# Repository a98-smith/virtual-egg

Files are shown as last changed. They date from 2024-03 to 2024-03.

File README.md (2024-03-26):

# Simulated Fragile Object (Virtual Egg)

## Project Description:

The Virtual Eggs Test (Clemente et al.,2015) was adapted from the Box and Blocks Test in order to evaluate the dexterity of sensory enabled prostheses. For their initial studies, origami boxes and spaghetti strands were used as their simulated fragile object (egg). This method of construction while informative, simple and cost effective has limitations for use outside of laboratory settings. For example, it would be potentially challenging for an individual with upper limb loss to construct or reset the aparatus without the presence of another individual which could impact engagement in 'in-the-wild' test scenarios.

In order to address this, this repo contains the [.stl](Assembly%20stls) and [technical drawings](Technical%20Drawings) for a passive and reusable egg design. The design can be altered to provide various levels of fragility, and can easily be reset and re-used with a single hand while requiring little to no manual dexterity.

The following section details the construction of the egg.

## Manufacturing and Assembly Instructions:

The egg consists of [6 main components](Technical%20Drawings/Assembly%20Drawings.pdf):
- **Shell:** The outer casing for the egg
- **Slide:** The sliding plates used to grasp the object
- **Midplate:** This is used as a back-board for the spring-loaded plates and combine with the Runner top ensure square travel.
- **GravLock:** Small pins used to lock the egg when too much force is applied (the egg is crushed) through gravity.
- **Runner:** Ensures square travel of the Slide throughout the range of motion.
- **Spring:** Provides a method of calibrating the fragility of the object, along with returning the Slide to it's original position.

### 1. Manufacture
The main structural components for the egg are 3D printed in PLA. The parts are designed with a low tolerance to ensure smooth travel, however some simple post-processing may be necessary for correct operation.

For each egg the printed parts list is:
- 2 x [**Shell**](Assembly%20stls/Shell.stl)
- 2 x [**Slide**](Assembly%20stls/Slide.stl)
- 1 x [**Midplate**](Assembly%20stls/Midplate.stl)

The remainder of the manufactured parts, are made from brass dowelling with a rounded end:
- 2 x **Runner** (⌀5.2mm)
- 4 x **GravLock** (⌀2mm)

The **Spring** should be a compression based spring, with an id > ⌀6mm, and an un-compressed length of ~30mm. The _k_-value of the **Spring** will determine the relative fragility of the egg and should be chosen with your experimental set-up in mind. 

### 2. Assembly
    
1. Affix **Runner** to central extrusion of **Slide** using an epoxy adhesive.
2. Insert **GravLock** into each hole on the bottom of the **Slides**.
3. Insert **Slide** into **Shell** ensuring the **GravLocks** are facing the correct direction (rounded end down).
4. Lubricate the contact surfaces of the **Shell** and **Runner**.
    - Both _Super Lube Multipurpose Synthetic Grease_ and fibreglass tape have proven to be effective in isolation but combined for best results.
5. Slot your selected **Spring** over the **Runner**, and the other end over the extrusion on **Midplate**.
6. Align the edges and adhere the back surface of **Shell** against **Midplate** maintaining gentle pressure.
7. Repeat this process for the second side.

> I hope this may be of use to someone, and if there are any questions or if anything about the process is unclear send me a message.

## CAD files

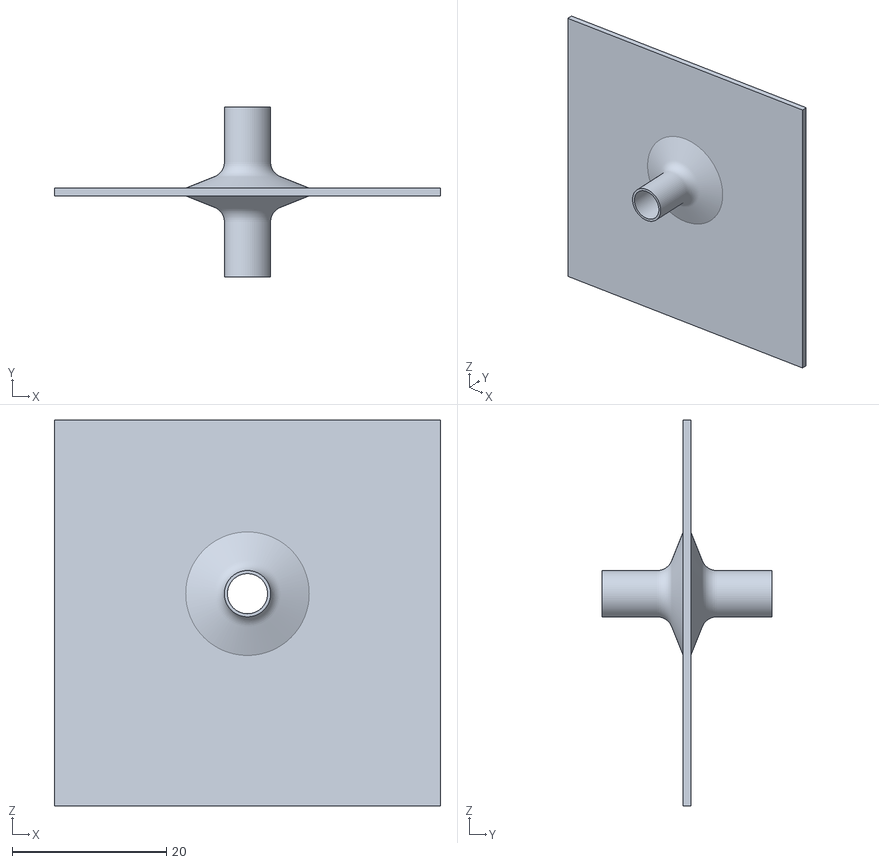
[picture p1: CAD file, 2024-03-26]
Assembly stls/Midplate.stl
50.0 x 22.0 x 50.0

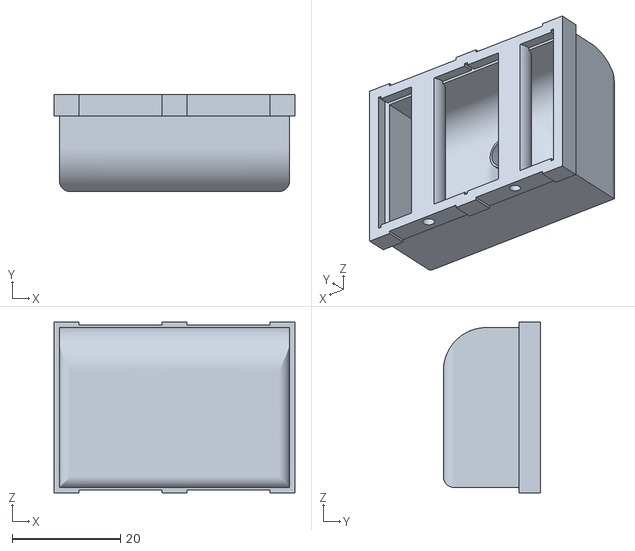
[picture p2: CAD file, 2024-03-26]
Assembly stls/Slide.stl
44.6 x 18.0 x 31.6

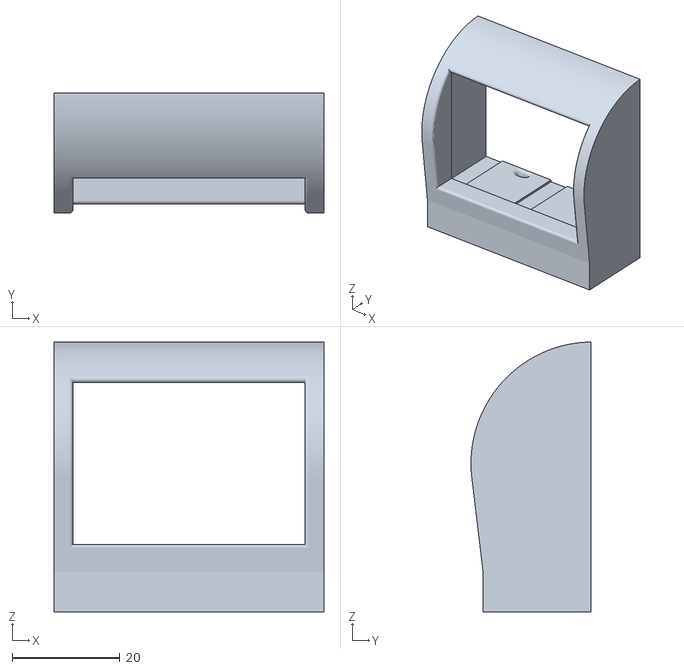
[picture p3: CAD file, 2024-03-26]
Assembly stls/Shell.stl
50.0 x 22.2 x 50.0

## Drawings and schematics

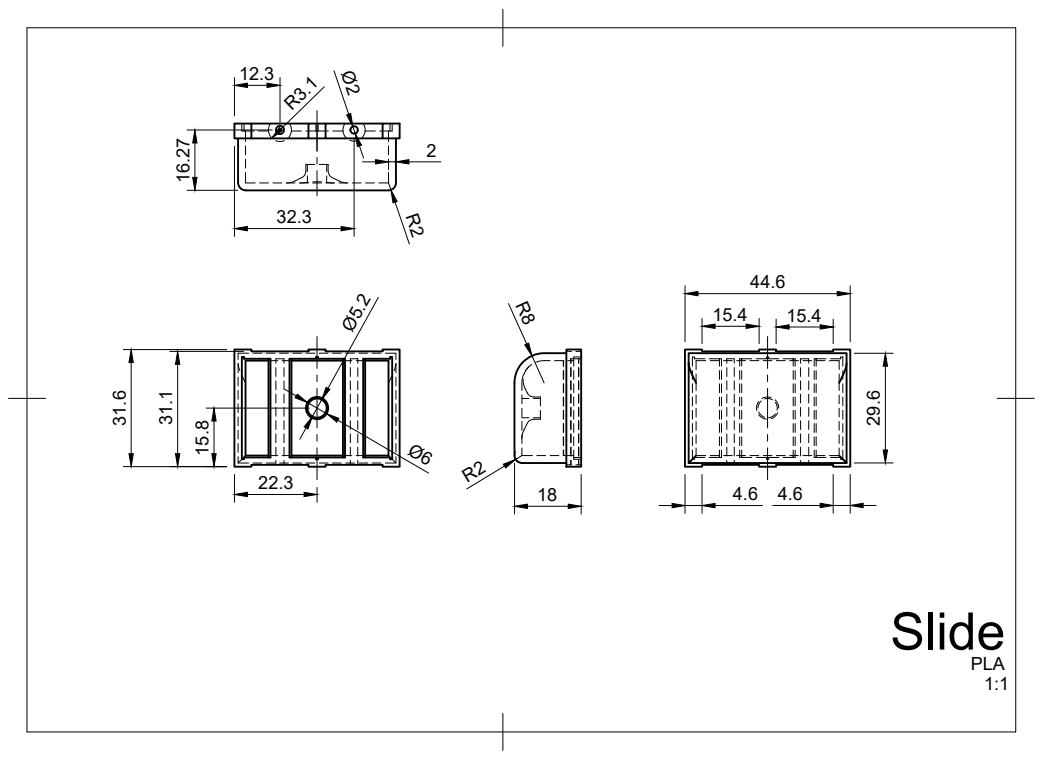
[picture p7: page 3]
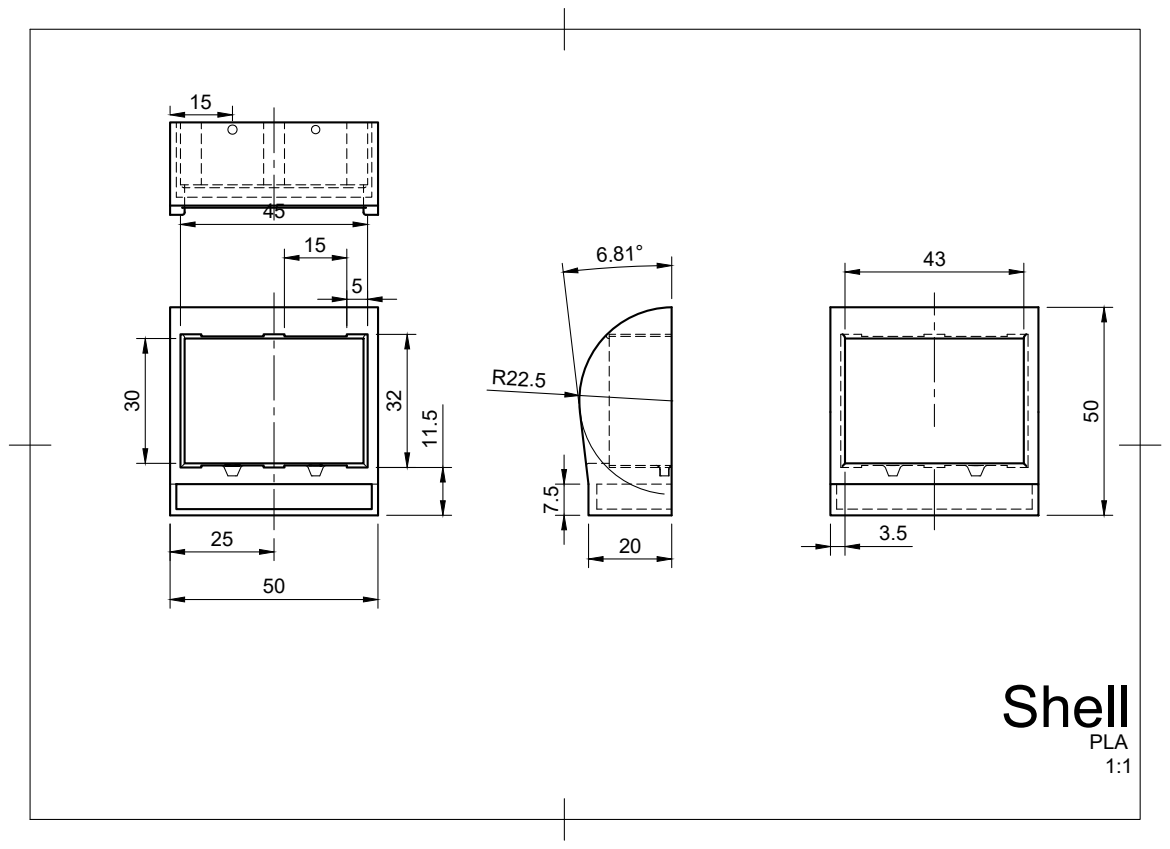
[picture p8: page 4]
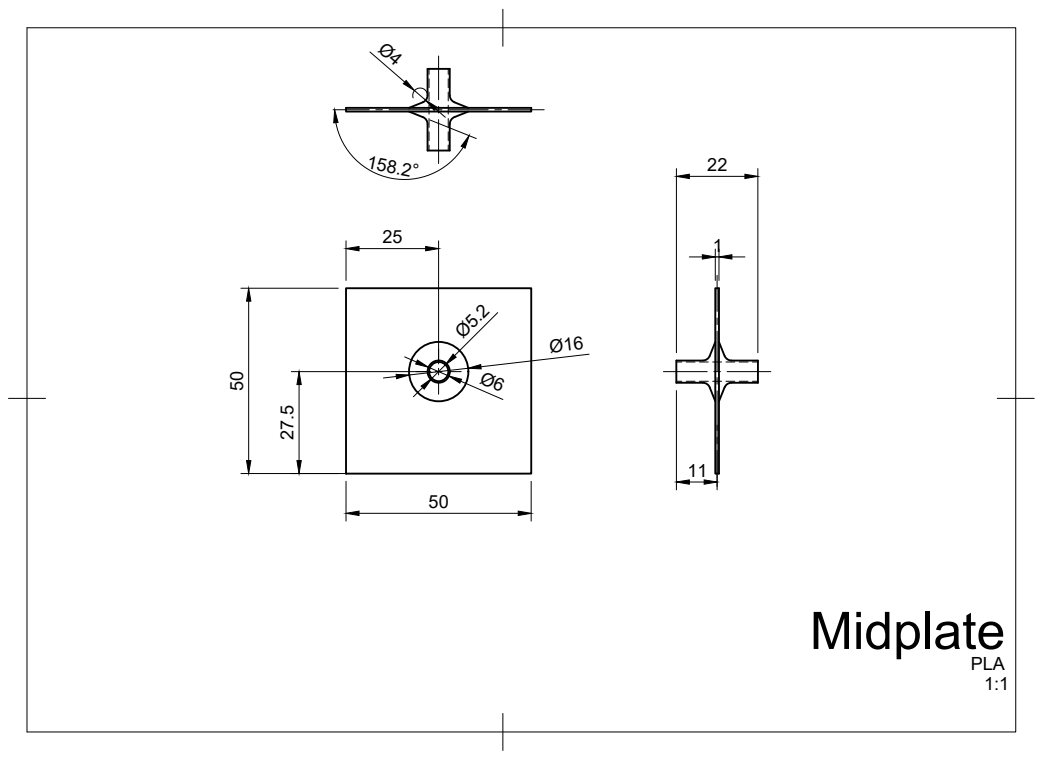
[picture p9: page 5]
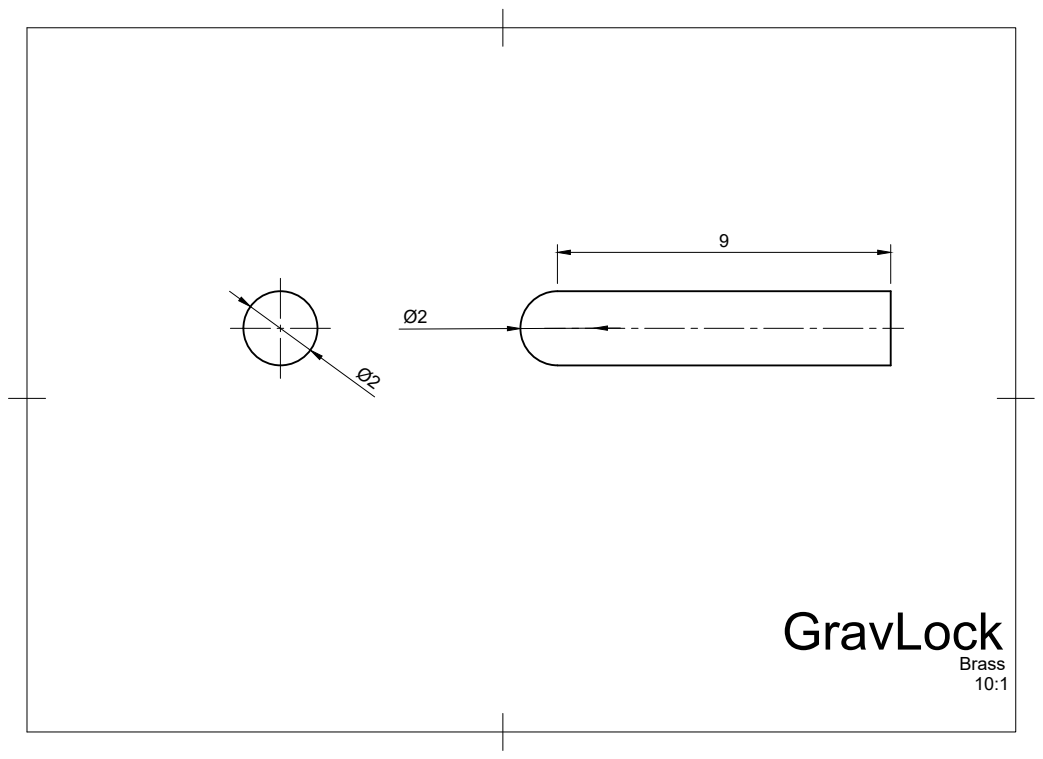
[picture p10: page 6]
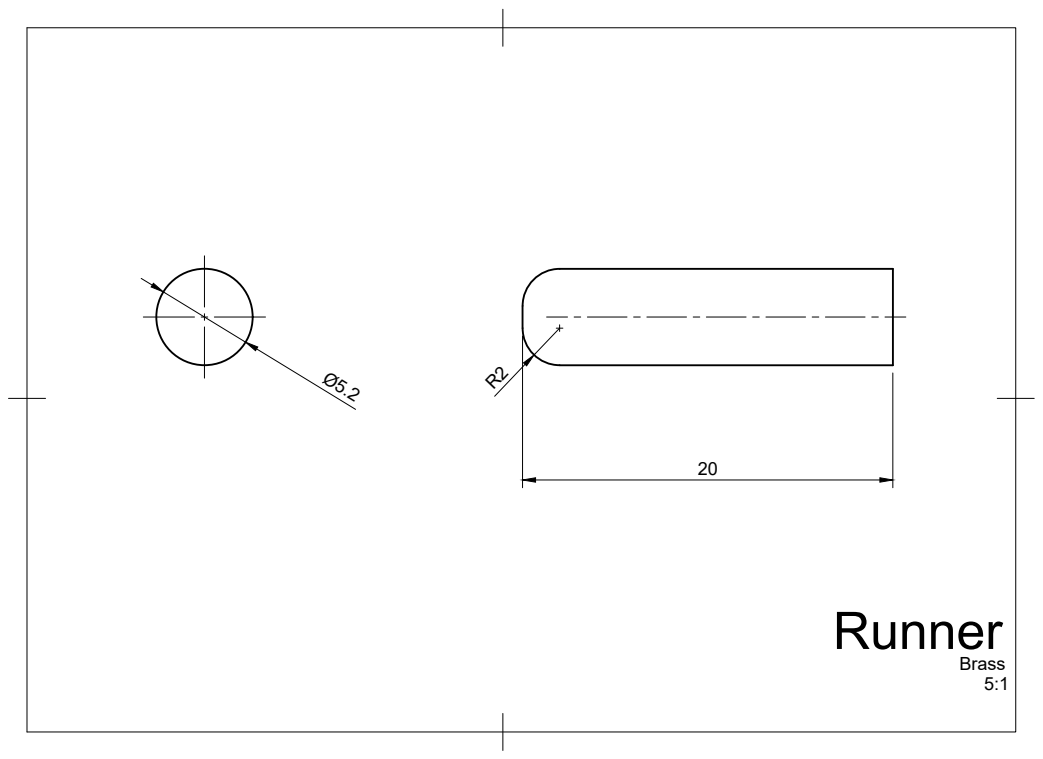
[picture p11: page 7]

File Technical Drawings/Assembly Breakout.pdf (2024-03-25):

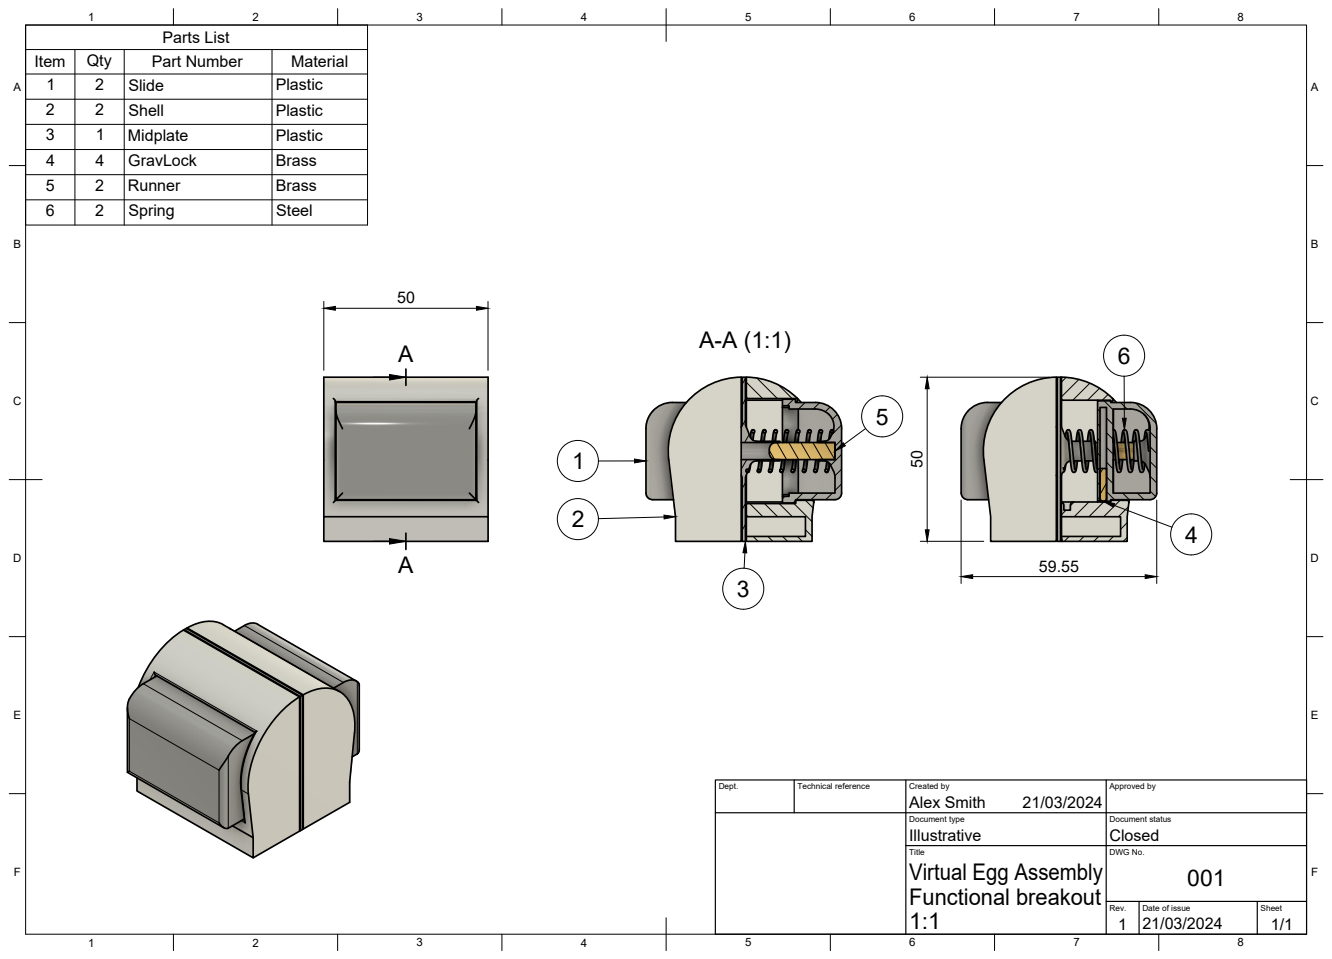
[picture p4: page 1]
Parts List

Item | Qty | Part Number | Material
1 | 2 | Slide | Plastic
2 | 2 | Shell | Plastic
3 | 1 | Midplate | Plastic
4 | 4 | GravLock | Brass
5 | 2 | Runner | Brass
6 | 2 | Spring | Steel

Dept. | Technical reference | Created by Alex Smith 21/03/2024 | Approved by

Document type Illustrative | Document status Closed

Title Virtual Egg Assembly Functional breakout 1:1 | DWG No. 001

Rev. 1 | Date of issue 21/03/2024 | Sheet 1/1

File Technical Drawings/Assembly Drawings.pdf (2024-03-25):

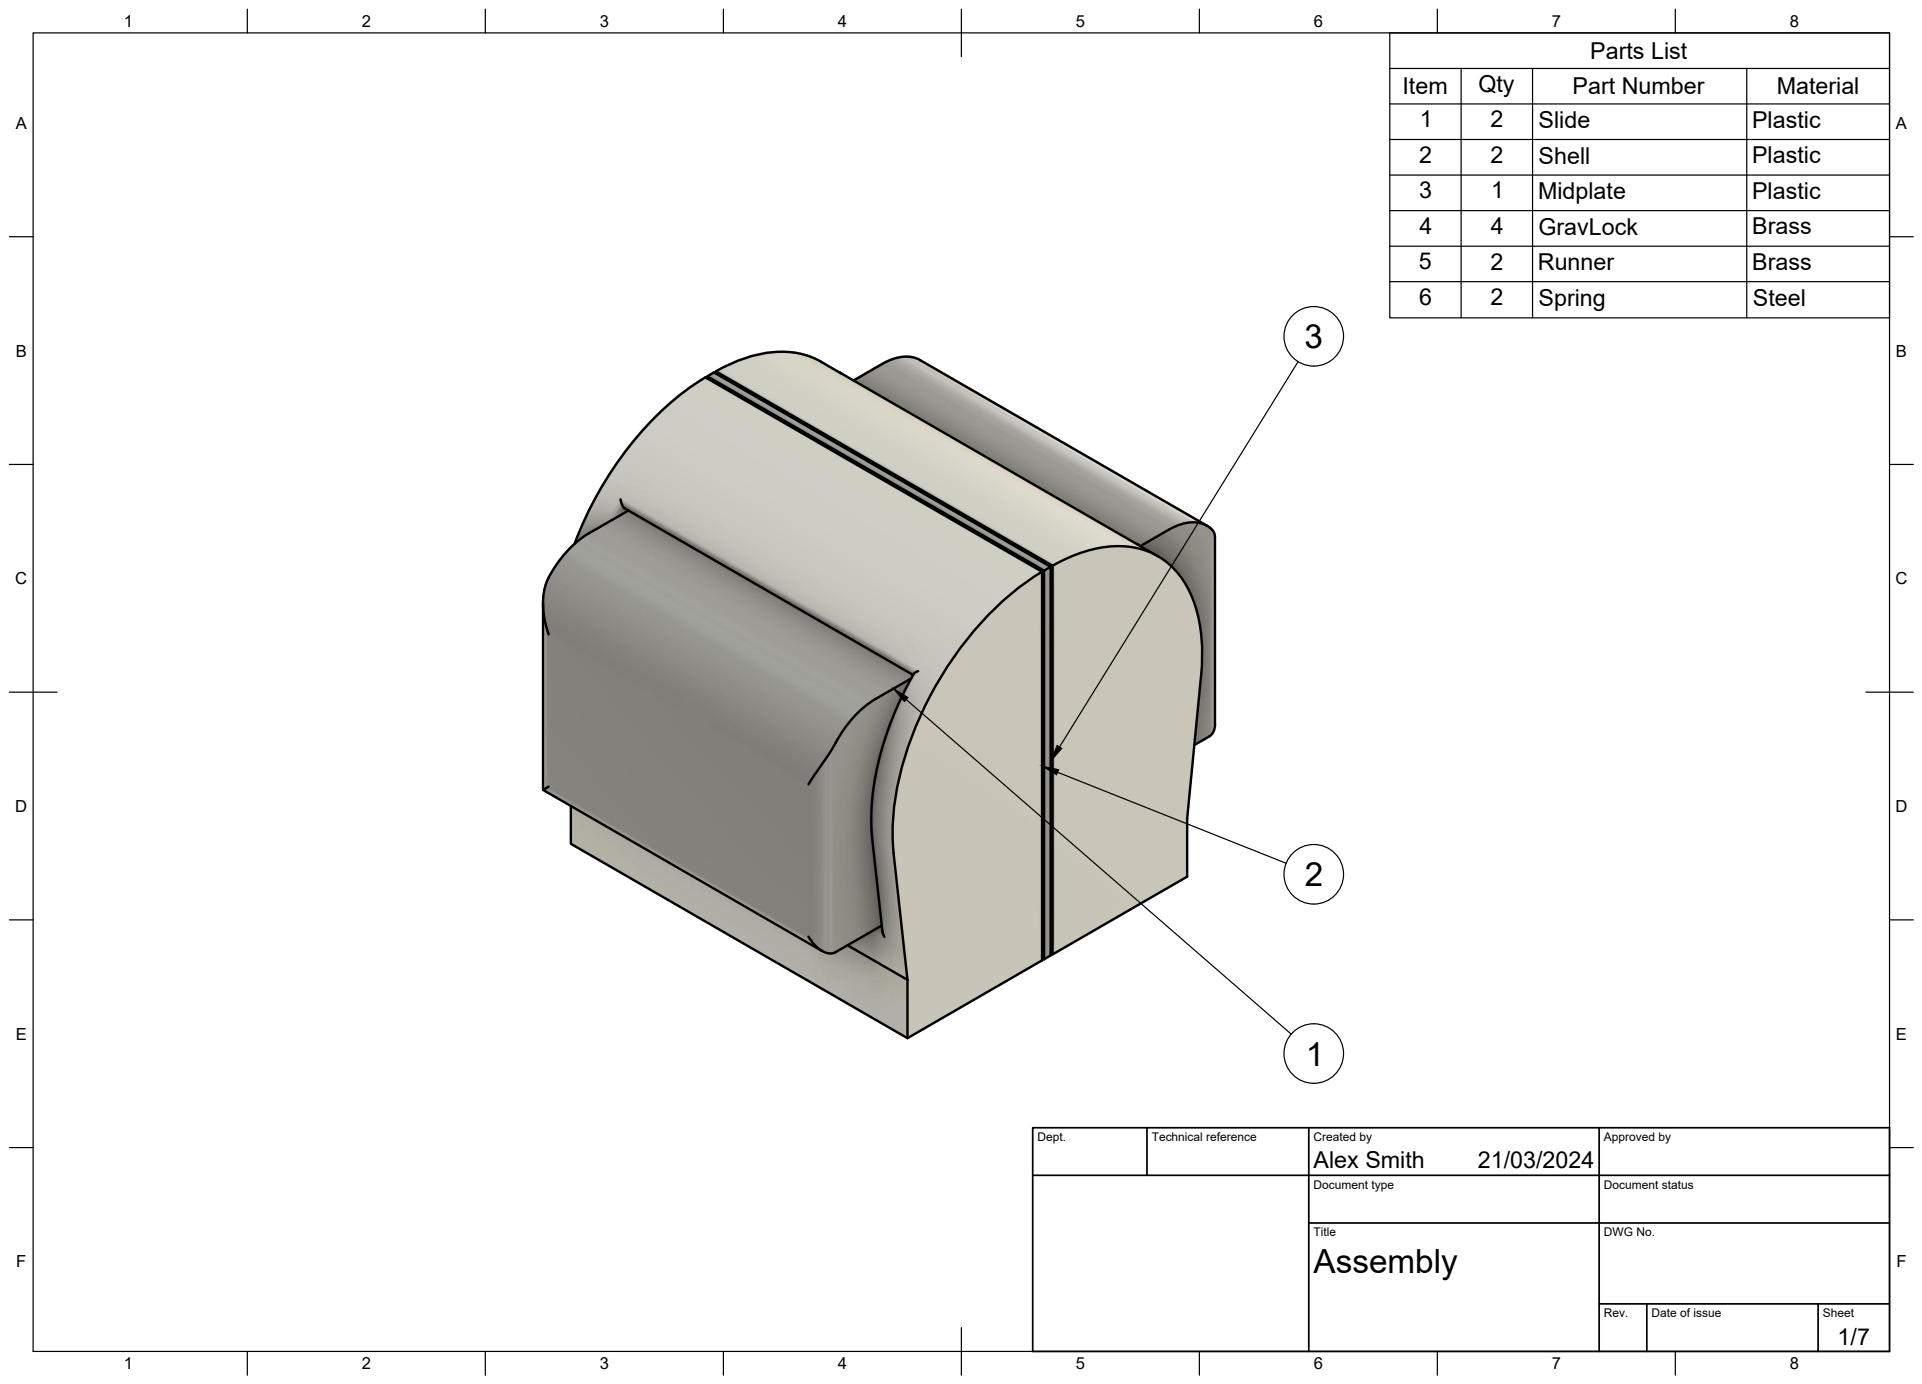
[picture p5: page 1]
Title; DWG No.; Rev.; Date of issue; Sheet; Parts List

Item | Qty | Part Number | Material
1 | 2 | Slide | Plastic
2 | 2 | Shell | Plastic
3 | 1 | Midplate | Plastic
4 | 4 | GravLock | Brass
5 | 2 | Runner | Brass
6 | 2 | Spring | Steel

Dept. | Technical reference | Created by Alex Smith 21/03/2024 | Approved by

Document type | Document status

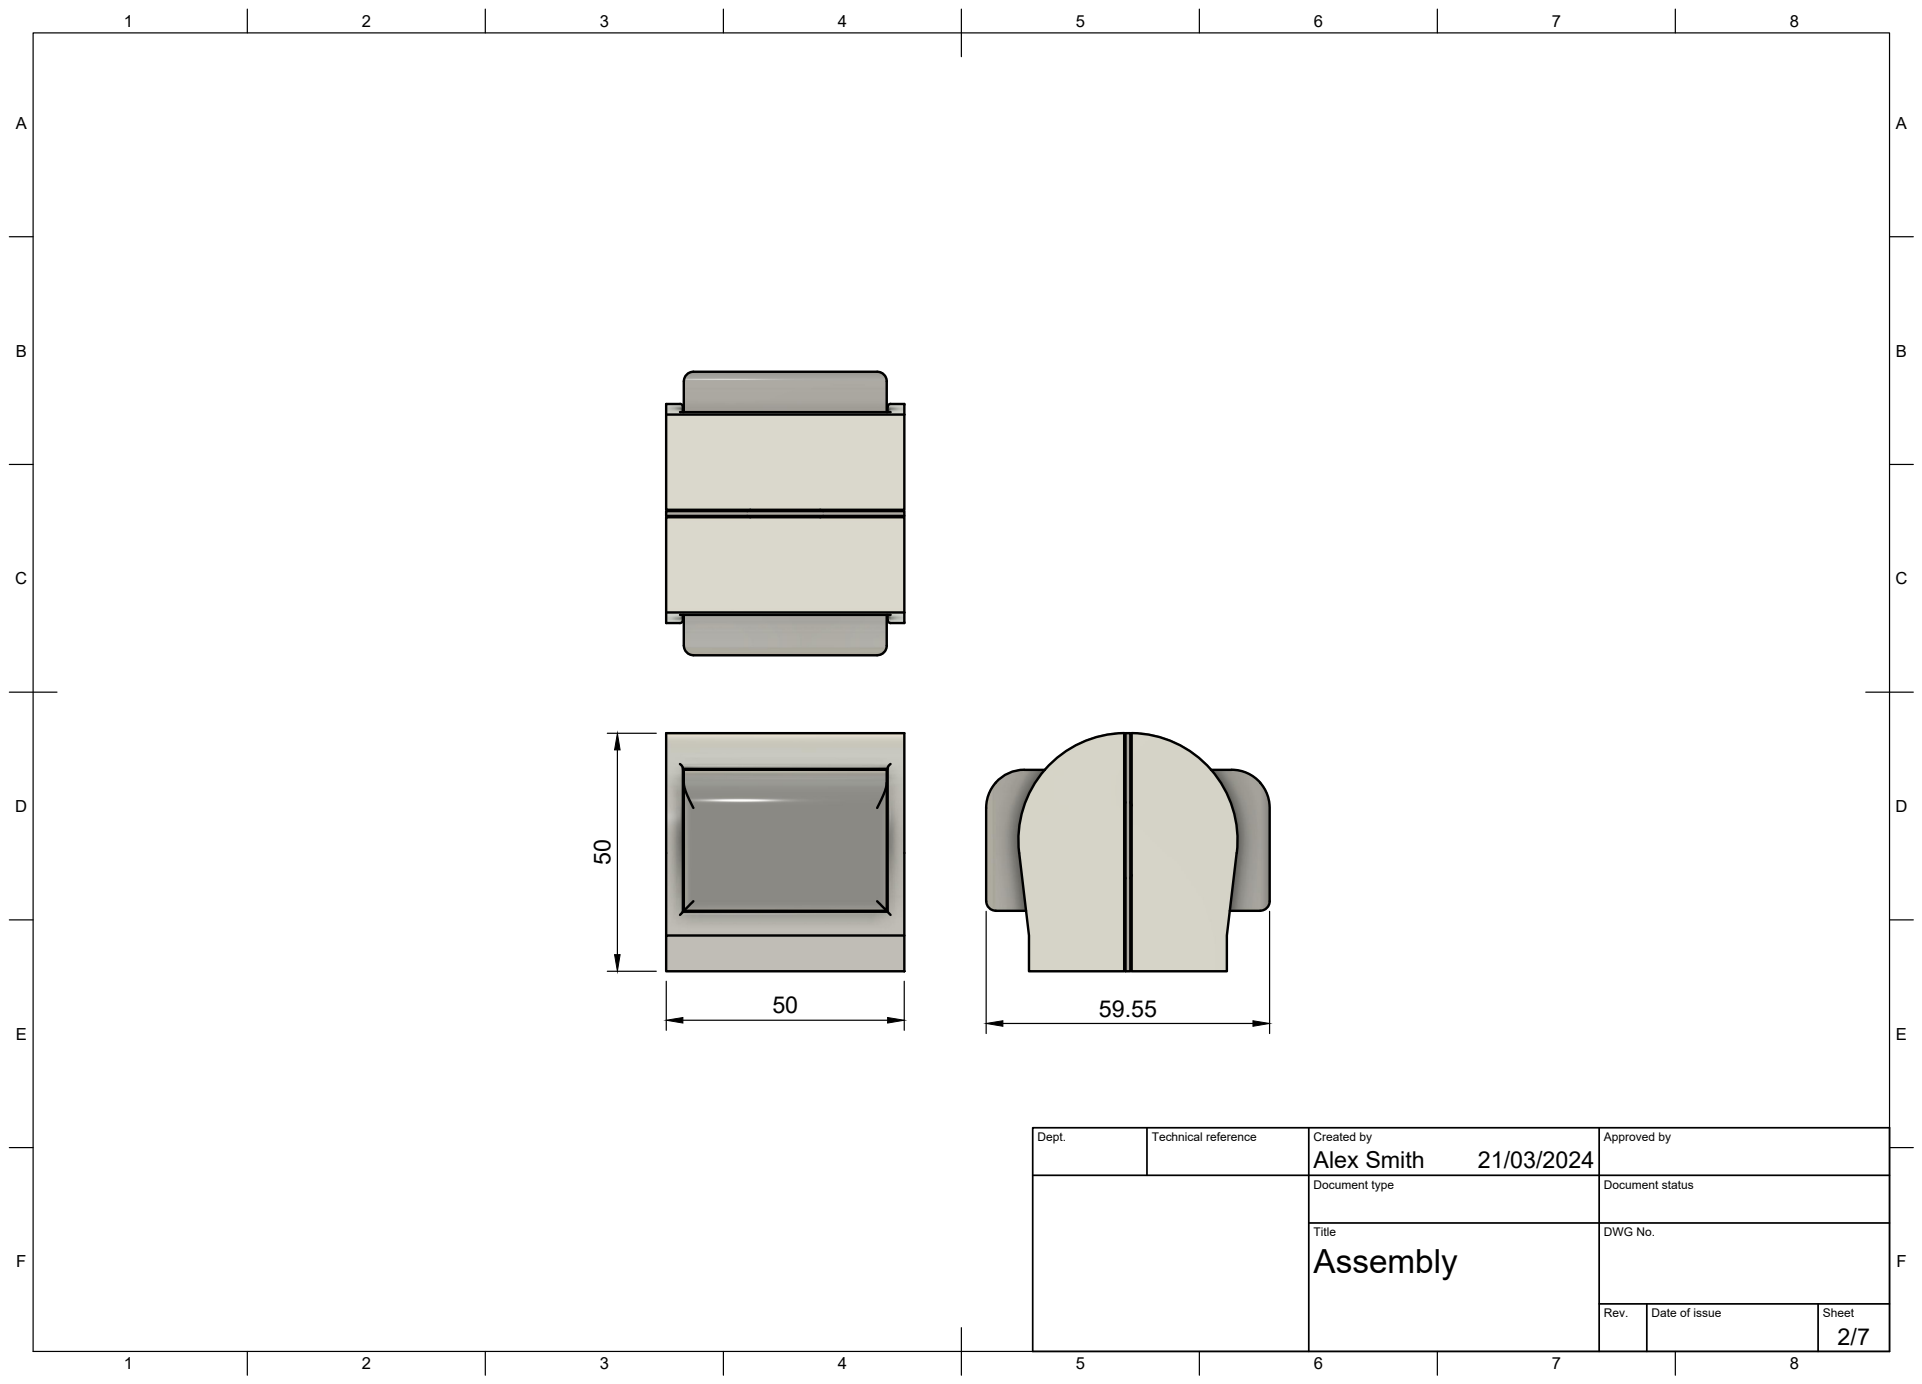
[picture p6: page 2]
Title; DWG No.; Rev.; Date of issue; Sheet

Dept. | Technical reference | Created by Alex Smith 21/03/2024 | Approved by

Document type | Document status
